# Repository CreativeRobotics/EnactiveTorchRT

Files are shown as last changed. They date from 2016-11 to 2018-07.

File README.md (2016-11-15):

# EnactiveTorchRT
The Enactive Torch Research Tool for enactive perception and sensory substitution research

The Enactive Torch project is a co-operative research endevour into sensory substitution and enactive perception. For full details of the project and its history take a look at the blog: https://enactivetorch.wordpress.com/

This repository is run by Creative Robotics Ltd who have developed the latest version of the Enactive Torch, the RT-RT (Research Tool)

For more information and details of how to purchase an Enactive Torch pleace contact Creative Robotics Ltd: sales@creative-robotics.com

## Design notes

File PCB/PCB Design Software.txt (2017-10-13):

We use DesignSpark PCB from RS Electronics to design all our PCB's. DesignSpark can be downloaded and used for free from the RS DesignSpark website here:
https://www.rs-online.com/designspark/pcb-software

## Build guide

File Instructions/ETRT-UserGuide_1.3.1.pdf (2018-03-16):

www.creative-robotics.com | support@creative-robotics.com

Table of Contents

Copyright © Creative Robotics Ltd 2016

Enactive Torch Research Tool ET-RT instructions
Document version 1.3.1

Device overview
The Enactive Torch contains an internal inertial measurement unit and Bluetooth module allowing data to be streamed from the device to a computer. The internal battery is charged via the USB port. The standard sensor head contains a rangefinder with a maximum 1.5 meter range, a narrow beam LED and a light sensor, and the sensor angle relative to the body of the ET-RT can be adjusted.

The device is equipped with an internal haptic actuator called a Linear Resonant Actuator or LRA. This is mounted in the case just below the user button. A pair of 3.5mm jack sockets on the right of the device allow for two external LRA’s to be plugged in and independently controlled. When an LRA is plugged into ‘Haptic Actuator 1’ socket it will disconnect the internal one and prevent it from operating.

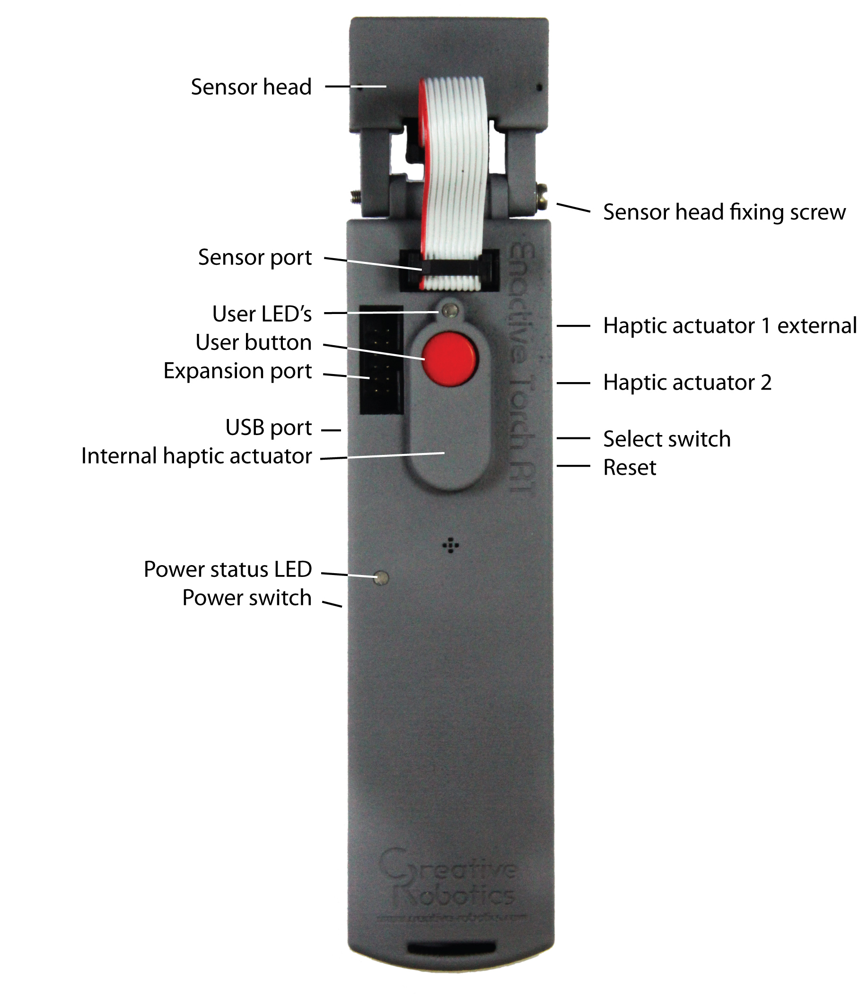
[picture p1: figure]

In software ‘Haptic Actuator 1’ is called LRA1 and ‘Haptic Actuator 2’ is called LRA2.

ET-RT instructions
Document version 1.3.1

Connecting to Bluetooth
The device should be marked with its Bluetooth name on a label on the rear of the case.
When connecting to it via Bluetooth ensure that the ET-RT is switched on and look for the device name. Data is transferred over Bluetooth using the Synchronous Serial Protocol (SSP). The serial port needs to be configured as follows:
- Baud rate 38400
- 1 stop bit
- No parity.

Commands
The ET software incorporates a limited set of commands for configuring the device remotely. These can be sent from a serial terminal or suitable piece of software using the Bluetooth link. By default the device will begin by transmitting a device information statement that includes the firmware version and the status of the internal sensors and user input.

The following serial commands are available and should be sent as ASCII characters followed by a line feed character. These commands are defined in the ETRT-System.h file used to compile the firmware. Any adjustments made to the ET-RT using these commands will not persist after the device is restarted.

Software name | Description | Character
CMD_GET_DEVICE_INFO | Get device information | ?
CMD_PRINT_CALIBRATION_DA TA | Print calibration values for gyroscopes and accelerometers | c
CMD_DATA_STREAM_ON | Turn data streaming on | D
CMD_DATA_STREAM_OFF | Turn data streaming off | d
CMD_SET_DATA_STREAM_RA W | Set data stream type to raw data | r
CMD_SET_DATA_STREAM_YPR | Set data stream type to YPR (Yaw Pitch Roll) | y
CMD_SET_DATA_STREAM_QUA TERNION | Set data stream type to Quaternion data | q

ET-RT instructions
Document version 1.3.1

Using the ET-RT
This section applies to devices with the latest firmware installed. Current version: 1.3

Data Formats
The example software that is supplied with the ET can output three different types of data generated by the internal sensors in addition to the data generated by the external sensor. By default it will output raw data from the internal sensors. Each packet of data is sent as human readable comma separated floating point values in a line terminated by a line feed and carriage return character. Each line is prefixed with a character indicating the type of data being sent.

Quaternion orientation data and the Roll Pitch and Yaw angles are estimates produced by combining the internal sensor reading from the gyroscopes, accelerometers and magnetometers. These estimated are computed by the device and can be subject to error. The system for estimating the orientation will also take a few seconds to converge on a solution.

Note: The system for generating Quaternions and Yaw, Pitch and Roll is under development and should not be relied on for accurate data. We recommend that you use the raw data format.
Each type of packet is formatted as follows. The letter r, y or p starts each line and indicates the data type:

Raw data format (Raw data from each internal sensor):

r, Accelerometer X, Accelerometer Y, Accelerometer Z, Gyro X, Gyro Y, Gyro Z, Magnetometer X, Magnetometer Y, Magnetometer Z, Rangefinder, LRA1 Intensity

YPR Format (Yaw Pitch and Roll estimate derived from internal sensors)

y, Yaw, Pitch, Roll, Rangefinder, LRA1 Intensity

Quaternion Format (Quaternion orientation data derived from internal sensors)

q, Quaternion 1, Quaternion 2, Quaternion 3, Quaternion 4, Rangefinder, LRA1 Intensity

Data ranges:

Sensor | Units | Range
Accelerometer | g | +/- 2
Gyroscope | Degrees per second | +/-250
Magnetometer | MilliGauss | +/-48000
Rangefinder | Raw Analogue Data | 0-1023

ET-RT instructions
Document version 1.3.1

Basic operation
Switch the ET-RT on. The status LED will illuminate red. It will begin transmitting raw data from the gyroscopes, accelerometers and sensor. This data can be read by connecting to the device from a computer via Bluetooth.

Press the red button to enable the haptic actuator (LRA). The device will map data from the rangefinder to the haptic actuator. The firmware has two modes of operation that can be changed with the selector switch.

Position 0: (switch pushed to the rear of the device) The range of an object is translated into vibration intensity where a shorter range will equate to greater intensity.

Position 1: (Switch pushed forward) The range translates into intensity but the haptic actuator delivers pulses rather than a continuous signal.

If the external LRA is plugged into haptic actuator socket 1 then it will respond. If no external actuator is plugged in then the internal one will respond.

Adjusting the sensor head angle
The sensor head can be tilted through approximately 180 degrees about the horizontal axis. This can be achieved by loosening the screw holding the head to the body. Take care not to try and adjust the head when the screw is tight. Applying too much force could cause damage to the plastic case.

Charging the battery
The battery is charged via the USB port so it can be charged by simply plugging the device into a USB port on a computer or into a USB mobile device charger. The status LED will illuminate green if the device is charged or orange if the device is charged and switched on.

ET-RT instructions
Document version 1.3.1

Programming
To write software and program the ET-RT download the Arduino IDE from here:

https://www.arduino.cc/en/Main/Software

You will also need to install the ET-RT device library and sensor drivers in the Arduino libraries folder. The device library, sensor drivers and examples are available here:

https://github.com/CreateiveRobotics/EnactiveTorchRT

To download your software connect the ET-RT to a USB port, switch it on and allow the device drivers to install.

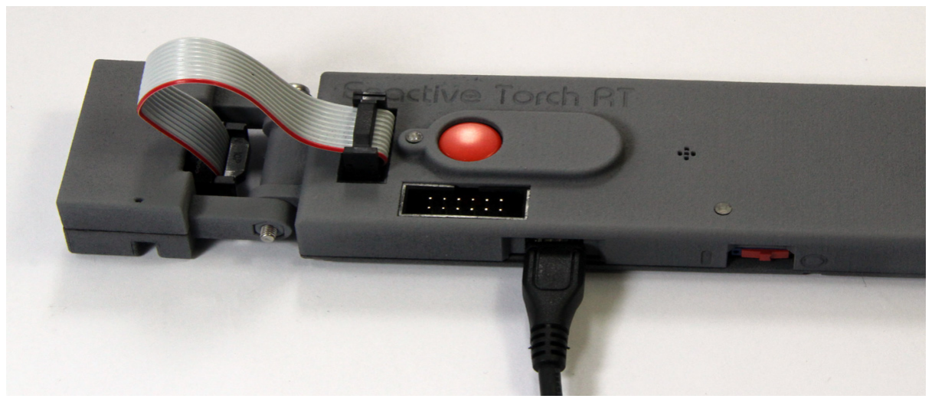
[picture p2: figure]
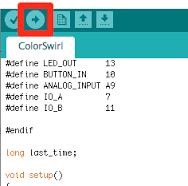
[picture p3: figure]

In the Arduino IDE select Tools > Board > LillypadUSB

Next select Tools > Port and look for your device. It should appear as a Lillypad USB.

To compile and upload your software click the upload button. When uploading the user LED will flicker orange red and green.

For more details please refer to the Arduino website.

ET-RT instructions
Document version 1.3.1

API Documentation
The core ET-RT functions are defined in the ETRTSystem class defined in the ‘ETRT-System.h’ library file.

The system class only controls the internal sensors for the device. To use the sensor head a device driver class is required. The API for the standard sensor is in the next section.

ETRTSystem(void)

Class constructor

void initialise()

Initialises the ET-RT System object. This does NOT initialise the inertial measurement unit. But it will initialise the Bluetooth serial port and the USB serial port. USB serial is initiated with a baud rate of 115200k

void initialiseImu(int32_t gbx, int32_t gby, int32_t gbz, int32_t abx, int32_t aby, int32_t abz)

Initialise the inertial measurement unit with calibration values for the gyros and accelerometers.
Accepts the following arguments in this order:
Gyro bias X
Gyro bias Y
Gyro bias Z
Accelerometer bias X
Accelerometer bias Y
Accelerometer bias Z

void update()

Update the ET-RT system. This updates the inertial measurement unit, processes any commands in the serial buffer and update any haptic effects. This needs to be called approximately every 10 milliseconds Using the standard Arduino delay(time) function will interfere with this but an alternative delay function waitFor(time) is available that will continuously call the update() function whilst providing a timed delay to your software.

ET-RT instructions
Document version 1.3.1

void setLed1(bool state)

Set the state of User LED 1.
1 = On, 0 = Off.

void setLed2(bool State)

Set the state of User LED 2.
1 = On, 0 = Off.

void Led1On()

Switch LED1 On

void Led1Off()

Switch LED1 Off

void Led2On()

Switch LED2 On

void LED2Off()

Switch LED1 Off

bool isButtonPressed()

Check the user button.
Returns 1 if pressed and 0 if not pressed.

bool getSwitchState()

Check the select switch.
Returns 1 if in the forward position and 0 if in the backward position.

bool getBluetoothState()

Read the connection status of the Bluetooth radio.
Return 1 if connected, 0 if not connected.

void beep(int pitch, int duration)

Produces an audio tone for a length of time specified in milliseconds.

ET-RT instructions
Document version 1.3.1

void enableLra1()

Enable haptic controller number 1

void disableLra1()

Disable haptic controller number 1

void setLra1(uint16_t intensity)

Set the vibration intensity of haptic controller number 1. This will call the appropriate enable or disable function at the same time so there is no need to enable the haptic controller first. Accepts a value in the range 0 to 1023.

void enableLra2()

Enable haptic controller number 2

void disableLra2()

Disable haptic controller number 2

void setLra2(uint16_t intensity)

Set the vibration intensity of haptic controller number 2. This will call the appropriate enable or disable function at the same time so there is no need to enable the haptic controller first. Accepts a value in the range 0 to 1023.

void pulseLra1(int intensity, int milliTime)

Create a vibration pulse for a specified time on haptic controller 1. This function will return immediately but the update() must be called every 10ms or more to allow the haptic pulse to complete.
Accepts an intensity value in the range 0 to 1023 and a time in milliseconds.

void pulseLra2(int intensity, int milliTime)

Create a vibration pulse for a specified time on haptic controller 2. This function will return immediately but the update() must be called every 10ms or more to allow the haptic pulse to complete.
Accepts an intensity value in the range 0 to 1023 and a time in milliseconds.

ET-RT instructions
Document version 1.3.1

void printIMURawData()

Print the raw inertial measurement data over the Bluetooth link. Data is in floating point format as comma separated values in the following order:
Accelerometer X, Y, Z, Gyroscope X, Y, Z, Magnetometer X, Y, Z
No line feeds or character returns are included.

void printIMUYPRData()

Prints the Yaw Pitch and Roll data over the Bluetooth link. Data is in floating point format as comma separated values in the following order:
Yaw, Pitch, Roll
No line feeds or character returns are included.

void printIMUQuaternionData()

Prints four quaternion values that describe the device orientation over the Bluetooth link. Data is in floating point format as comma separated values in the following order:
Q1, Q2, Q3, Q4
No line feeds or character returns are included.

void printCalibrationValues()

Prints the calibration values for the device over the Bluetooth link. Data is in floating point format as comma separated values in the following order:
Gyro X, Y, Z, Accelerometer X, Y, Z
No line feeds or character returns are included.

void printDeviceInfo()

Prints device information over the Bluetooth link. The following data is printed as individual lines:
- Device firmware version
- IMU initialisation status
- Magnetometer initialisation status
- Data stream enable state
- Button state
- Switch state

ET-RT instructions
Document version 1.3.1

float getQ(uint8_t index)

Returns one of four quaternion values.
Accepts a value from 0 to 3 representing quaternions 1, 2, 3 and 4.

void waitFor(long int delayMillis)

A function that will delay your program for the specified time but allow the ET system to continue updating in the background. Use instead of the standard Arduino delay() function. Accepts a delay time in milliseconds.

ET-RT instructions
Document version 1.3.1

Standard sensor API

ETRTRangefinderS1(void)

Constructor

void initialise(bool enableState)

Initialise the sensor. Accepts an argument to determine if the rangefinder is enabled. Send 1 to enable or 0 to disable on startup.

void update(void)

Update the readings and filtered values

int getRange()

Returns the raw rangefinder reading

int getRangeFiltered()

Returns a filtered version of the rangefinder reading

int getLight()

Get the raw light sensor reading.

int getLightFiltered()

Get a filtered version of the light sensor reading.

void setLed(int ledValue)

Set the LED torch with an intensity in the range 0-255.

void LedOn()

Switch the LED torch on.

void ledOff()

Switch the LED torch off.

void enable()

Enable the rangefinder.

ET-RT instructions
Document version 1.3.1

void disable()

Disable the rangefinder.

void setEnable(bool state)

Set the rangefinder enable state. Send 1 to enable or 0 to disable.

bool getEnableState()

Get the state of the rangefinder. Returns 1 if enabled or 0 if disabled.

void setRangeFilterLength(int length)

Set the length of the filter (Number of samples to average over)

void setLightFilterLength(int length)

Set the length of the filter (Number of samples to average over)

ET-RT instructions
Document version 1.3.1

Sensor response
The rangefinder produces a voltage that is proportional to an object in its field of view. This response is NOT linear but conforms to the table below.

The sensor outputs a voltage that is read by an analogue to digital converter. The function getRange() returns the value generated by the analogue to digital converter.

In order to convert this value to one that represents a voltage it must be scaled according to the resolution of the analogue converter which is 10 bits, or a maximum value of 1023, and the operating voltage of the device which is 3.3 volts.

This mapping can be done as follows:

Analogue to voltage scaling | 3.3 ÷ 1023 = 0.0032258
Voltage to analogue scaling | 1023 ÷ 3.3 = 310
To convert an analogue reading of 523 to a voltage: | Voltage = 523 × 0.0032258 = 1.7393934 Volts

To convert a voltage of 1.9 volts into the raw analogue value: ADCValue = 1.9 × 310 = 589

ET-RT instructions
Document version 1.3.1

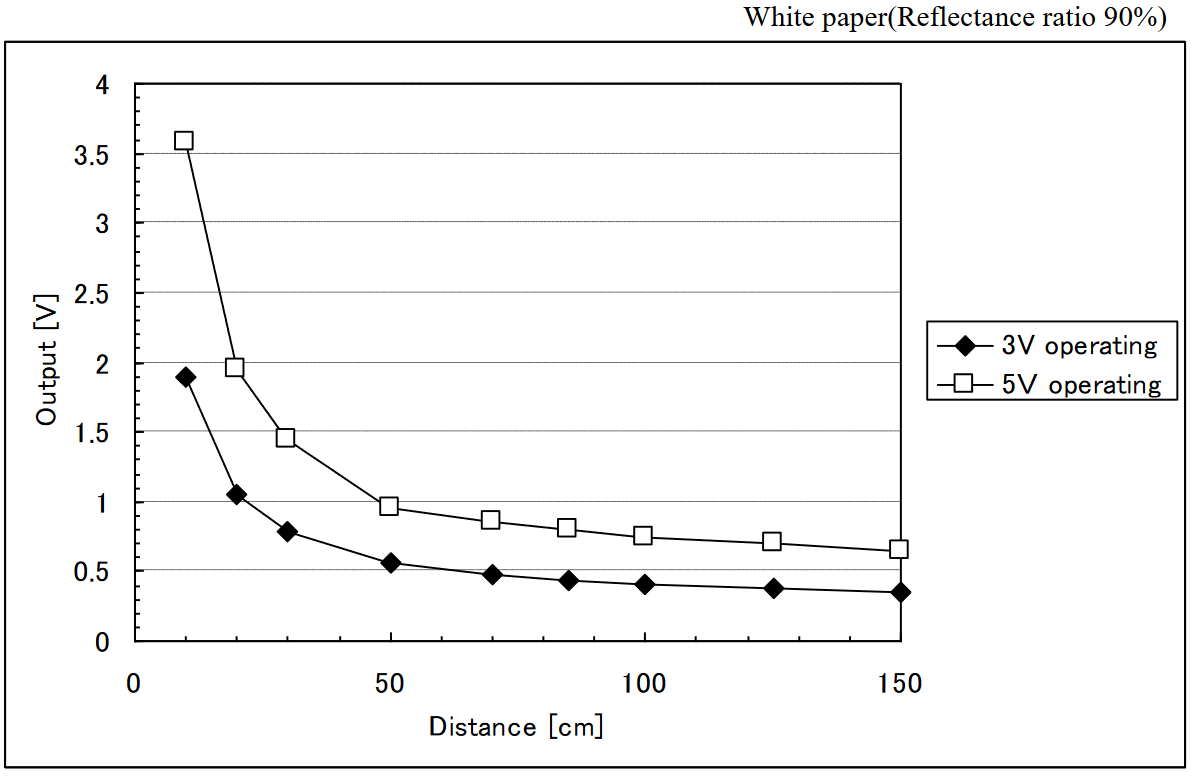
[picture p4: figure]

Inertial Measurement Unit Axis
The diagram below illustrates the axis orientation of the gyroscope and accelerometers.

ET-RT instructions
Document version 1.3.1

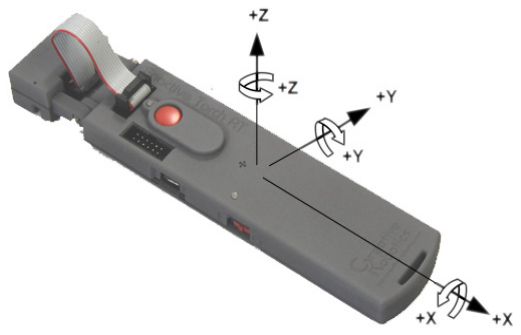
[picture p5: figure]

DISCLAIMER OF LIABILITY
While we always try to provide accurate information, there may be times when factual, technical or typographical inaccuracies appear in our documentation. We apologise if this happens and we reserve the right to make changes and corrections at any time, without notice. Creative Robotics expressly disclaims liability for errors or omissions in the content of this document and makes no commitment to update the information contained on these sites.
Creative Robotics expressly disclaims all liability for the interpretation and use by others of any information contained in this document. All products are subject to change without prior notice. Creative Robotics disclaims any responsibility for errors, omissions or inaccuracies in product documentation or any other data relating to our products. Creative Robotics disclaims any responsibility for loss, damage or harm caused directly or indirectly by the use of our products.
(Basically: be careful, have fun but if you mess up then don’t blame us)

ET-RT instructions
Document version 1.3.1

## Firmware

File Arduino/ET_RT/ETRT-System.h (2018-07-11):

//ET-RT Device Class
#define FIRMWARE_VERSION    "0.1.1"

#ifndef _ETRTSystem_H_
#define _ETRTSystem_H_
#endif
#include "ETRT-MPU9250.h"
#include <inttypes.h>
#include <EEPROM.h>
#include <TimerOne.h>
/*
Timer1 used for fast PWM on the LRA pins
Timer1.initialize(40); // 40 us = 25 kHz

*/


//#define DEBUG //comment in for debud data over bluetooth - uses 3%
//#define IMUInitLoop //repeatedly try and init the imu if not working

//Bits for the interrupt on change port (if used)
#define PUSHBUTTON_BIT        1
#define DIGITAL_SENSOR2_BIT   2
#define AUXD2_BIT             3
#define AUXD10_BIT            4
#define AUXD9_BIT             5

//Serial port settings
#define BLUETOOTH_SPEED         38400
#define USB_SPEED         			115200

#define Bluetooth         			Serial1
#define USB               			Serial
#define Debug										Bluetooth //Define which serial port to use for debug messages
#define USB_MIRROR
//Bluetooth Commands;
//buffer locations for command processing
#define MAIN_COMMAND 0
#define SUB_COMMAND  1
//MAIN COMMANDS
#define CMD_GET_DEVICE_INFO							'?'
#define CMD_PRINT_CALIBRATION_DATA			'c'
#define CMD_DATA_STREAM_ON							'D'
#define CMD_DATA_STREAM_OFF							'd'
#define CMD_SET_DATA_STREAM_RAW 				'r'
#define CMD_SET_DATA_STREAM_YPR					'y'
#define CMD_SET_DATA_STREAM_QUATERNION	'q'
//Pin asignments
const uint8_t userLED1_pin			= 17;
const uint8_t userLED2_pin			= 30;
const uint8_t userButton_pin		= 15;
const uint8_t btStatus_pin			= 13;

const uint8_t selectSwitch_pin		= 4;
const uint8_t LRA1PWM_pin			= 10;
const uint8_t LRA2PWM_pin			= 11;
const uint8_t LRA1EN_pin			= 22;
const uint8_t LRA2EN_pin			= 23;
const uint8_t ImuInt_pin			= 7;
const uint8_t audioOut_pin			= 12; //piezo resonator

//Pins for external IO - these are usually left alone for their own driver to handle

const uint8_t digitalSensor0_pin	= 5; //
const uint8_t digitalSensor1_pin	= 16; //PWM
const uint8_t analogSensor0_ch		= 0; //analog chanel
const uint8_t analogSensor1_ch		= 1; //analog chanel
const uint8_t AuxD0_pin				= 6;
const uint8_t AuxD1_pin				= 14;
const uint8_t AuxD2_pin				= 9;
const uint8_t AuxD3_pin				= 8;
const uint8_t AuxA0_ch				= 2; //analog chanel
//Analog Pins
#define BUFFER_LENGTH 128

//Quaternion filter values
// These are the free parameters in the Mahony filter and fusion scheme, Kp
// for proportional feedback, Ki for integral
#define Kp 2.0f * 5.0f
#define Ki 0.0f
//------------------------------------------
enum dataStreamType{
	RawData = 0,
	YPRData,
	QuaternionData
};

enum lraState{
	LraOff = 0,
	LraBraking,
	LraOverdriving,
	LraOn
};
const uint8_t LRA_RESPONSE = 30; //minimum time for LRA response
const uint8_t LRA_OVERDRIVE = 128; //ammount of PWM to overdrive the LRA when starting
const uint16_t LRA_MAX = 1023; //maxumum PWM value
const uint16_t LRA_MIN = 512; //minimum PWM needed to start LRA - a 50% duty cycle -- was 544?
static volatile bool imuNewDataflag = 0;  
static volatile uint16_t imuIntTotal = 0;

void IMU_ISR();
//------------------------------------------

class ETRTSystem{
	public:

	ETRTSystem(void)	{setupPins();}
	void initialise();
	void initialiseImu(int32_t gbx, int32_t gby, int32_t gbz, int32_t abx, int32_t aby, int32_t abz);
	void update(); //update the whole system
	void setLed1(bool state);
	void setLed2(bool State);
	
	void Led1On()					{setLed1(1);}
	void Led1Off()				{setLed1(0);}
	void Led2On()					{setLed2(1);}
	void LED2Off()				{setLed2(0);}
	
	bool isButtonPressed()						{return !digitalRead(userButton_pin);}
	bool getSwitchState()						{return digitalRead(selectSwitch_pin);}
	bool getBluetoothState()				{return !digitalRead(btStatus_pin);}
	void beep(int pitch, int duration)	{tone(audioOut_pin, pitch, duration);}
	void enableLra1()								{digitalWrite(LRA1EN_pin, 1);}
	void disableLra1()							{digitalWrite(LRA1EN_pin, 0);}
	void setLra1(uint16_t intensity);
	void enableLra2()								{digitalWrite(LRA2EN_pin, 1);}
	void disableLra2()							{digitalWrite(LRA2EN_pin, 0);}
	void setLra2(uint16_t intensity);
	
	void pulseLra1(int intensity, int milliTime);
	void pulseLra2(int intensity, int milliTime);
	void printIMURawData();
	void printIMUYPRData();
	void printIMUQuaternionData();
	void printCalibrationValues();

	void printDeviceInfo();
	float getQ(uint8_t index);
	
	

	void waitFor(long int delayMillis);//delay for the specified time - keeps updating the system while the delay runs
	MPU9250 imu;
	
	uint8_t dataStreamType = QuaternionData;
	//int printDelay 							= 100;
	bool dataStreamEnable 			= 0;
	int declination 						= 0.0; //-1.28 For creative Robotics	
	uint8_t floatPrecision 			= 3;
	
	bool newData = 0;//flag indicating new imu data
	
	private: //=-----------------------------------------------------------------------------------------------	
	void updateHaptics();
	void setupPins();
	void updateBluetooth(); //update the serial port and process any pending commands
	void printCmdErr();
	void printCmdAck();
	void initialiseIMU();
	//void imuSelfTest();
	bool updateImu();
	void updateQuaternions();
	void updateYPR();
															
	void MahonyQuaternionUpdate(float ax, float ay, float az, float gx, float gy,
                            float gz, float mx, float my, float mz,
                            float deltat);
	//void initialiseI2C();
	bool buttonState 						= 0; //the state of the user button
	bool switchState 						= 0; //the position of the user switch
	bool BTStatus 							= 0;
	bool imuInitialised 				= 0;
	bool magInitialised 				= 0;
	
	//LRA control parameters - used to update haptics in the background so functions return immediatly
	uint16_t lra1Duty = 0, lra2Duty = 0;
	long int lra1Timer = 0, lra2Timer = 0;
	uint8_t lra1State = LraOff, lra2State = LraOff;
	long int nextLra1Update = 0, nextLra2Update = 0;
	long int pulseLength1 = 0, pulseLength2 = 0;
	bool pulse1Active = 0, pulse2Active = 0;
	//Quaternion Filters

	float GyroMeasError 				= PI * (40.0f / 180.0f);
	// gyroscope measurement drift in rad/s/s (start at 0.0 deg/s/s)
	float GyroMeasDrift 				= PI * (0.0f  / 180.0f);

	float beta 									= sqrt(3.0f / 4.0f) * GyroMeasError;   // Compute beta
	// Compute zeta, the other free parameter in the Madgwick scheme usually
	// set to a small or zero value
	float zeta 									= sqrt(3.0f / 4.0f) * GyroMeasDrift;

	// Vector to hold integral error for Mahony method
	float eInt[3] 							= {0.0f, 0.0f, 0.0f};
	// Vector to hold quaternion
	float q[4] 									= {1.0f, 0.0f, 0.0f, 0.0f};
};

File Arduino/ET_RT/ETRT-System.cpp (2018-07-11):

#include <ETRT-System.h>

void IMU_ISR(){
  imuNewDataflag = 1;
  imuIntTotal++;
}


//#include "Arduino.h"

void ETRTSystem::initialise(){
	//init pins
	setupPins();
	Wire.begin();
	Wire.setClock(400000L);
	Serial1.begin(BLUETOOTH_SPEED);
	Serial.begin(USB_SPEED);
	Timer1.initialize(40); // 40 us = 25 kHz
	Timer1.pwm(LRA1PWM_pin, 0);
	Timer1.pwm(LRA2PWM_pin, 0);
	delay(100);
	
}

void  ETRTSystem::initialiseImu(int32_t gbx, int32_t gby, int32_t gbz, int32_t abx, int32_t aby, int32_t abz){
	imu.gyro_bias[0] = gbx;
	imu.gyro_bias[1] = gby;
	imu.gyro_bias[2] = gbz;
	imu.accel_bias[0] = abx;
	imu.accel_bias[1] = aby;
	imu.accel_bias[2] = abz;
	
	initialiseIMU();
	#ifdef IMUInitLoop
	while(!imuInitialised || !magInitialised){
		delay(500);
		initialiseIMU();
	}
	#endif
	attachInterrupt(digitalPinToInterrupt(ImuInt_pin), IMU_ISR, RISING);
}



void ETRTSystem::setupPins(){
	pinMode(selectSwitch_pin, INPUT_PULLUP);
	pinMode(userButton_pin, INPUT_PULLUP);
	pinMode(AuxD0_pin, INPUT_PULLUP);
	pinMode(AuxD1_pin, INPUT_PULLUP);
	pinMode(AuxD2_pin, INPUT_PULLUP);
	pinMode(AuxD3_pin, INPUT_PULLUP);
	pinMode(btStatus_pin, INPUT);
	pinMode(audioOut_pin, OUTPUT);

	pinMode(LRA1EN_pin, OUTPUT); 
	pinMode(LRA2EN_pin, OUTPUT); 
	//pinMode(LRA1PWM_pin, OUTPUT); 
	//pinMode(LRA2PWM_pin, OUTPUT);
}
//-_-_-_-_-_-_-_-_-_-_-_-_-_-_-_-_-_-_-_-_-_-_-_-_-_-_-_-_-_-_-_-_-_-_-_
void ETRTSystem::update(){
	updateBluetooth();
	updateHaptics();
	if(updateImu()){
		updateQuaternions();
		updateYPR();
		newData = 1; //this can be checked and cleared by the user sketch
	}
}
//-_-_-_-_-_-_-_-_-_-_-_-_-_-_-_-_-_-_-_-_-_-_-_-_-_-_-_-_-_-_-_-_-_-_-_
void ETRTSystem::setLed1(bool state){
	if(state == 1) RXLED0;//digitalWrite(USERLED_1, 0);
	else RXLED1;//digitalWrite(USERLED_1, 1);
}
//-_-_-_-_-_-_-_-_-_-_-_-_-_-_-_-_-_-_-_-_-_-_-_-_-_-_-_-_-_-_-_-_-_-_-_

void ETRTSystem::setLed2(bool state){
	if(state == 1) TXLED0;//digitalWrite(USERLED_2, 0);
	else TXLED1;//digitalWrite(USERLED_2, 1);
}
//-_-_-_-_-_-_-_-_-_-_-_-_-_-_-_-_-_-_-_-_-_-_-_-_-_-_-_-_-_-_-_-_-_-_-
void  ETRTSystem::setLra1(uint16_t intensity){
	if(millis() < nextLra1Update) return; //prevent updates happening too fast
	nextLra1Update = millis()+LRA_RESPONSE; //set the next minimum time between updates
	//Map intensity (0-1023) to viable WM (512-1023)
	lra1Duty = map(intensity, 0, 1023, LRA_MIN, LRA_MAX);//(intensity/2)+LRA_MIN;
	
	//activate brake if intensity is zero, or exit of lra is already off
	if(lra1State == LraOff && lra1Duty <= LRA_MIN) return; //do nothing if everything is off
	else if(lra1Duty <= LRA_MIN){
		Timer1.setPwmDuty(LRA1PWM_pin, 0); //zero PWM
		lra1State = LraBraking; ////set state to braking
	}
	else{
		switch(lra1State){
			case LraOff: //enable the device then set the duty cycle with overdrive and change the state
				enableLra1();
				Timer1.setPwmDuty(LRA1PWM_pin, constrain(lra1Duty+LRA_OVERDRIVE, 0, LRA_MAX));
				lra1State = LraOverdriving;
				break;
			case LraBraking: //switch back to overdrive - this should never happen because updates should always happen less frequently than braking period
				Timer1.setPwmDuty(LRA1PWM_pin, constrain(lra1Duty+LRA_OVERDRIVE, 0, LRA_MAX));
				lra1State = LraOverdriving;
				break;
			case LraOverdriving: //change the duty but keep overdriving unless zero - this shoud never happen because the update frequency should always be less than the time spent overdriving
				Timer1.setPwmDuty(LRA1PWM_pin, constrain(lra1Duty+LRA_OVERDRIVE, 0, LRA_MAX));
				break;
			case LraOn: //just change the duty cycle
				Timer1.setPwmDuty(LRA1PWM_pin, constrain(lra1Duty, 0, LRA_MAX));
				break;
		}
	}
	//set the timeout variable
	lra1Timer = millis()+LRA_RESPONSE;
}
//-_-_-_-_-_-_-_-_-_-_-_-_-_-_-_-_-_-_-_-_-_-_-_-_-_-_-_-_-_-_-_-_-_-_-_
void  ETRTSystem::setLra2(uint16_t intensity){
	if(millis() < nextLra2Update) return; //prevent updates happening too fast
	nextLra2Update = millis()+LRA_RESPONSE; //set the next minimum time between updates
	//Map intensity (0-1023) to viable WM (512-1023)
	lra2Duty = map(intensity, 0, 1023, LRA_MIN, LRA_MAX);//(intensity/2)+LRA_MIN;

	
	//activate brake if intensity is zero, or exit of lra is already off
	if(lra2State == LraOff && lra2Duty <= LRA_MIN) return; //do nothing if everything is off
	else if(lra2Duty <= LRA_MIN){
		Timer1.setPwmDuty(LRA2PWM_pin, 0); //zero PWM
		lra2State = LraBraking; ////set state to braking
	}
	else{
		switch(lra2State){
			case LraOff: //enable the device then set the duty cycle with overdrive and change the state
				enableLra2();
				Timer1.setPwmDuty(LRA2PWM_pin, constrain(lra2Duty+LRA_OVERDRIVE, 0, LRA_MAX));
				lra2State = LraOverdriving;
				break;
			case LraBraking: //switch back to overdrive - this should never happen because updates should always happen less frequently than braking period
				Timer1.setPwmDuty(LRA2PWM_pin, constrain(lra2Duty+LRA_OVERDRIVE, 0, LRA_MAX));
				lra2State = LraOverdriving;
				break;
			case LraOverdriving: //change the duty but keep overdriving unless zero - this shoud never happen because the update frequency should always be less than the time spent overdriving
				Timer1.setPwmDuty(LRA2PWM_pin, constrain(lra2Duty+LRA_OVERDRIVE, 0, LRA_MAX));
				break;
			case LraOn: //just change the duty cycle
				Timer1.setPwmDuty(LRA2PWM_pin, constrain(lra2Duty, 0, LRA_MAX));
				break;
		}
	}
	//set the timeout variable
	lra2Timer = millis()+LRA_RESPONSE;
}


void ETRTSystem::pulseLra1(int intensity, int milliTime){
	pulseLength1 = millis()+milliTime;
	pulse1Active = 1;
	setLra1(intensity);
}
void ETRTSystem::pulseLra2(int intensity, int milliTime){
	pulseLength2 = millis()+milliTime;
	pulse2Active = 1;
	setLra2(intensity);
}
//Update the haptic devices so they can be set and run in the background
void   ETRTSystem::updateHaptics(){
	//If the haptic is set to zero then the device must have a braking period of 30ms
	//If it is set to non zero then it has an overdrive period of 30ms
	//Check to see if a pulse command was sent - disable if pulse period has ended
	if(pulse1Active && millis() > pulseLength1){
		//end the pulse1Active
		setLra1(0);
		pulse1Active = 0;
	}
	if(pulse2Active && millis() > pulseLength2){
		//end the pulse1Active
		setLra2(0);
		pulse2Active = 0;
	}
	//if the current time has gone past the time when we need to update, then update
	if(lra1Timer < millis()){
		switch(lra1State){
			lra1Timer = millis()+LRA_RESPONSE; //reset the timer
			case LraBraking: //end braking period, disable the LRA
				//Bluetooth.println("BrakeEnd");
				Timer1.setPwmDuty(LRA1PWM_pin, 0);
				disableLra1();
				lra1State = LraOff;
				break;
			case LraOverdriving: //end overdrive period, set to the desired duty
				//Bluetooth.println("ODEnd");
				Timer1.setPwmDuty(LRA1PWM_pin, lra1Duty);
				lra1State = LraOn;
				break;
		}
	}
	if(lra2Timer < millis()){
		lra2Timer = millis()+LRA_RESPONSE;//reset the timer
		switch(lra2State){
			case LraBraking: //end braking period, disable the LRA
				Timer1.setPwmDuty(LRA2PWM_pin, 0);
				disableLra2();
				lra2State = LraOff;
				break;
			case LraOverdriving: //end overdrive period, set to the desired duty
				Timer1.setPwmDuty(LRA2PWM_pin, lra2Duty);
				lra2State = LraOn;
				break;
		}
	}
}
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

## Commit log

2016-11-15 CAD and Insctuctions
    [BOM 1A.ods, BoxLabels 1.csv, BoxLabels 1.ods, BoxLabels 2.csv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]
2016-11-15 Added calibration setch to examples
2016-11-18 Updated Instructions
    Added sections, system and sensor API's and more instructions on
    programming and charging.
2017-10-13 PCB software
    Added details of the PCB design software we use
2018-03-14 Updated system.h
    Removed printDelay variable
2018-03-15 Bug fix
    Fixed a bug in data printing. Added a code option to print iterative
    count for checking data packet sequential integrity
2018-03-16 Update instructions
    Updated instructions to include details of sensor units and scale.
    Updated firmware to include a firmware version number.
2018-07-17 Update
    Moved calibration values for all devices to calibration.h for ease of
    use.
